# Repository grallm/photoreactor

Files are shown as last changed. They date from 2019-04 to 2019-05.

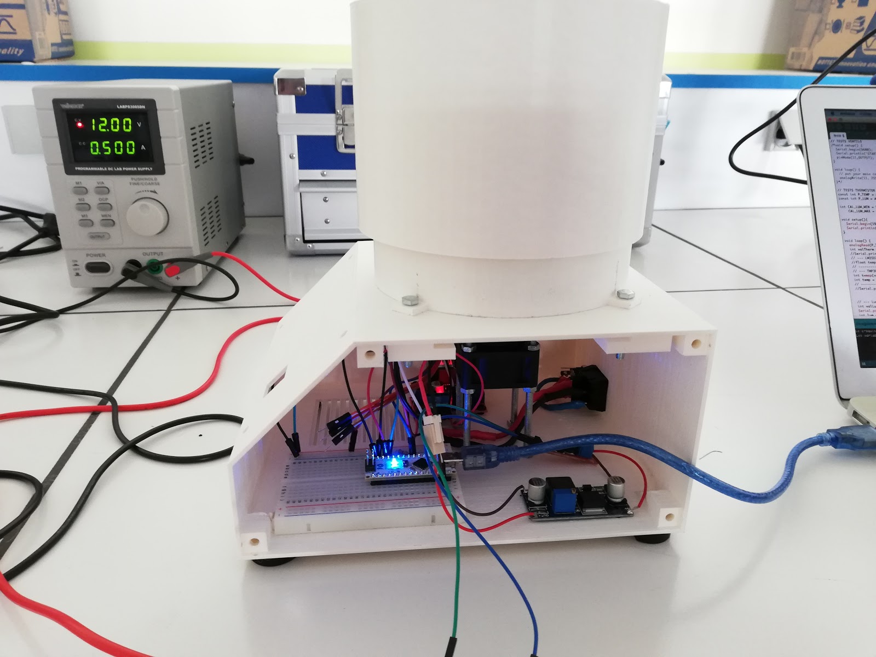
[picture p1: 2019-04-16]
images/finishing_assembly.jpg

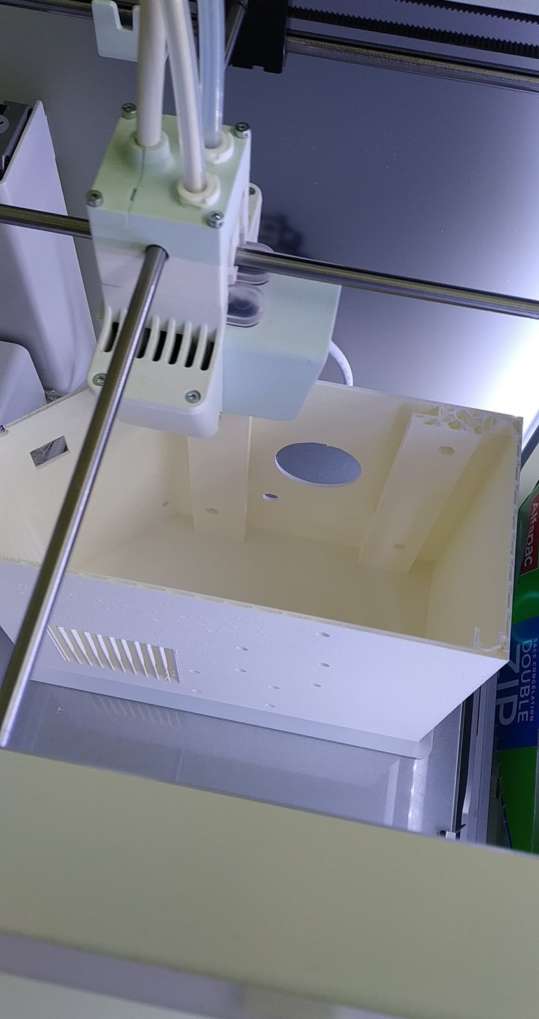
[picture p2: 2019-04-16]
images/box_printing.jpg

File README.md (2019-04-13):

# Photoreactor
Developed in first year of studies to accelerate chemical reactions

Original project https://gitlab.univ-nantes.fr/fablab

## Thanks
- Developed at [Fablab de la Faculté des Sciences de Nantes](https://gitlab.univ-nantes.fr/fablab)
- Requested by [Yann PELLEGRIN (Chemistry researcher at Université de Nantes)](https://www.univ-nantes.fr/version-francaise/yann-pellegrin-357721.kjsp)
- Developed by [Malo GRALL (@grallm)](https://github.com/grallm/), Théo BORDILLON and Moustafa KHEDIM
- With the preciouses advices and help of [Cédric DOUTRIAUX](https://gitlab.univ-nantes.fr/doutriaux-c) and [Frédéric GOUALARD](http://frederic.goualard.net/)

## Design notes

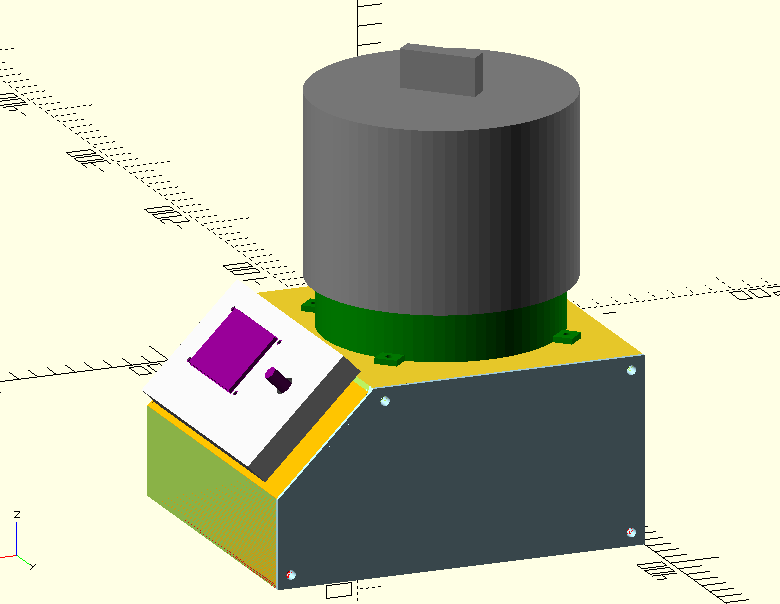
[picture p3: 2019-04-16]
images/fin3D-ext.27-03-19.png

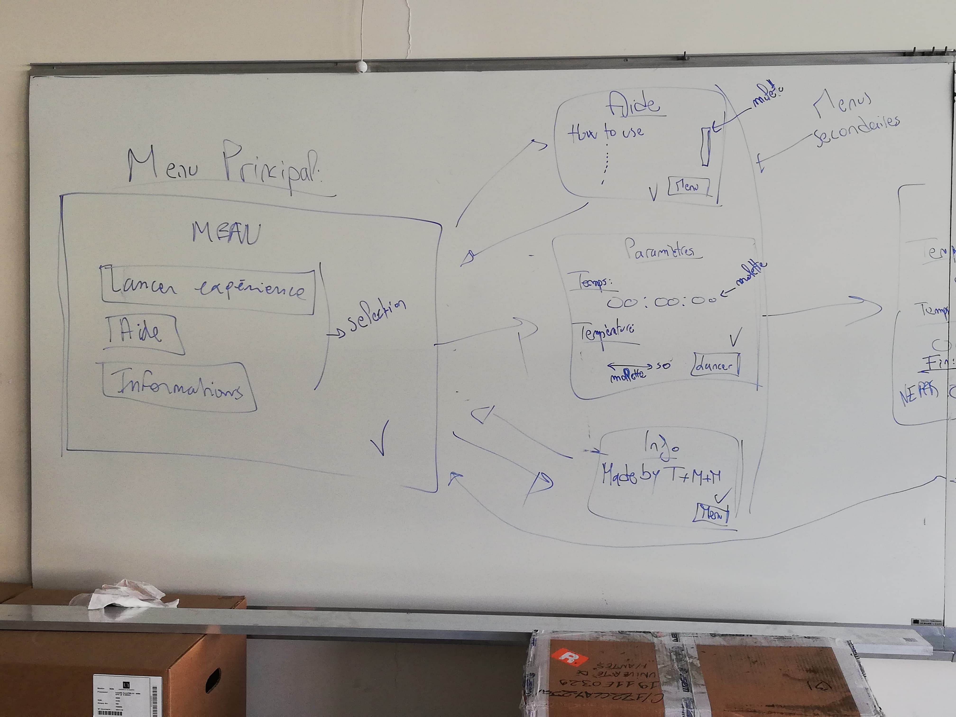
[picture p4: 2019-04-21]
images/menus_schema-1.jpg

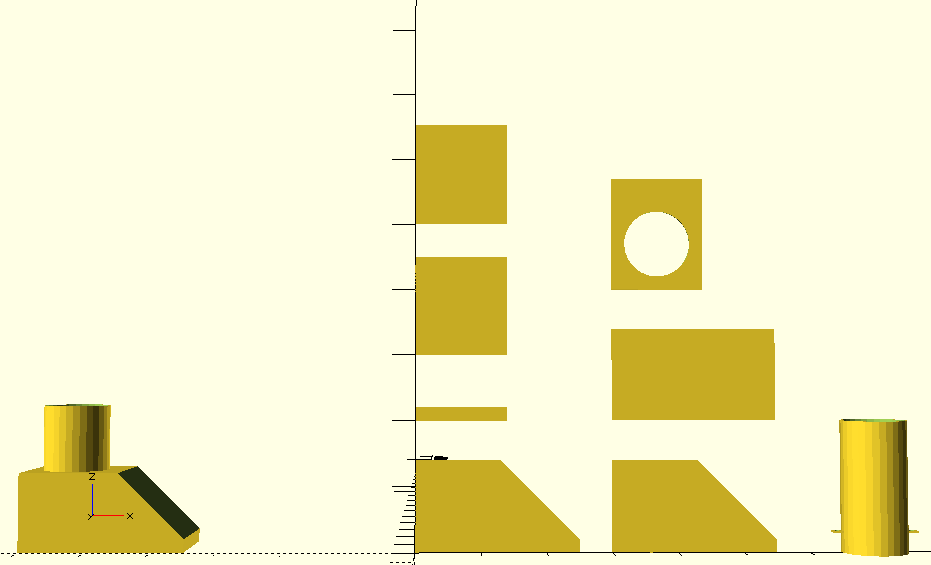
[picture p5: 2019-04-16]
images/Modèle 3D semaine 5.png

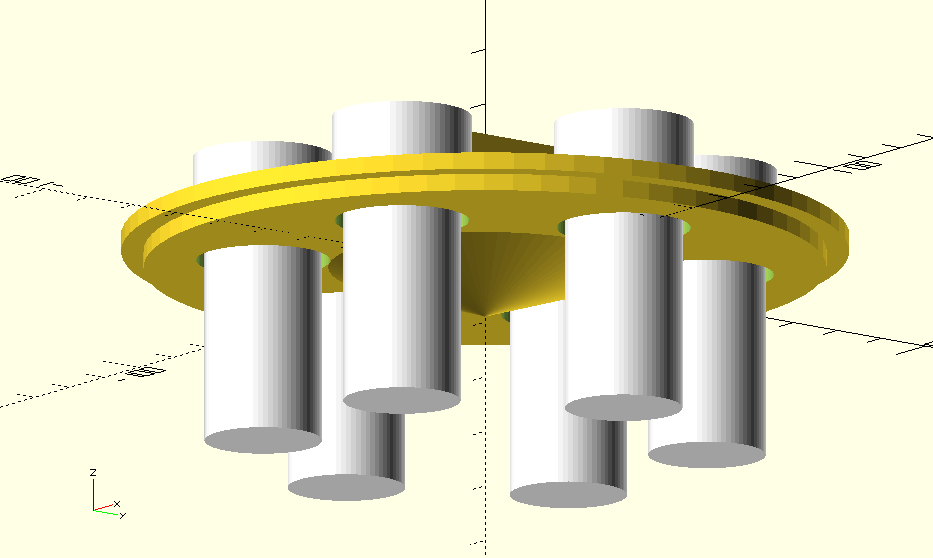
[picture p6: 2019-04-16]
images/grille-S11.png

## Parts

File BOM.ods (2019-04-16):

Projet photoréacteur (Théo Malo et Moustafa) |  |  | Prix total (euros) | 151.08 | Prix total unité (euros) (juste achats) | 91.58
Parties | Produit | Quantité | Lien | Site d'achat | Description | Prix (euros par unité) | Prix total (euros) | Vérifié (stock, coût)
Alimentation | Coupleur pour piles (18650) | 2 | https://www.gotronic.fr/art-coupleur-2-accus-18650-bh538-27840.htm | gotronic.fr | Si pas alimentation direct -> sur piles | 2.4 | 4.8 | OK
 | Piles 18650 | 4 | https://www.gotronic.fr/art-accu-li-ion-18650-2-5a-29250.htm | gotronic.fr | Si pas le droit alimentation | 9.9 | 39.6 | OK
 | OU alimentation 12V |  | https://www.gotronic.fr/art-adaptateur-ps1230-21193.htm | gotronic.fr |  |  | 0 | OK
 | Interrupteur | 1 | https://www.gotronic.fr/art-interrupteur-h8650-4226.htm | gotronic.fr |  | 1.7 | 1.7 | OK
 | Embout femelle pour alimentation (5,5x2,1mm) | 1 | https://www.gotronic.fr/art-embase-alim-sa215-14966.htm | gotronic.fr |  | 0.4 | 0.4 | OK
 | Attache mâle (Molex 2.54mm) | 1 | https://www.gotronic.fr/art-connecteur-s002-90.htm | gotronic.fr | Alimenter tiroir | 0.1 | 0.1 | OK
 | Attache femelle (Molex 2.54mm) | 1 | https://www.gotronic.fr/art-connecteur-p002-91.htm | gotronic.fr | Alimenter tiroir | 0.1 | 0.1 | OK
 | Abaisseur de tension | 3 | https://www.gotronic.fr/art-regulateur-ajustable-1-25-a-30-v-ef03061-23543.htm | gotronic.fr | Baisser tension depuis piles (14->12) et pour LED(12->2.3) | 3.15 | 9.45 | OK
Optique | LED | 2 | https://www.conrad.fr/p/roschwege-led-high-power-bleu-31-lm-130-23-v-700-ma-lsc-b-181827 | conrad.fr |  | 7.4 | 14.8 | OK
 | Radiateur | 1 | https://www.conrad.fr/p/dissipateur-pour-led-fischer-elektronik-sk-46-10-sa-10020378-24-kw-l-x-l-x-h-51-x-51-x-10-mm-1-pcs-188053 | conrad.fr | Accrocher LED dessus (pâte)(sur tiroir) | 1.93 | 1.93 | OK
 | Graisse conductrice | 1 | https://www.gotronic.fr/art-graisse-silicone-t12-5-6044.htm | gotronic.fr | Accrocher LED-radiateur | 2.5 | 2.5 | OK
 | Ventilateur | 1 | https://www.gotronic.fr/art-mf30101v2-28970.htm | gotronic.fr | Sous radiateur | 8.2 | 8.2 | OK
 | Pilote LED | 2 | https://www.gotronic.fr/art-driver-de-led-de-puissance-com-13716-24815.htm | gotronic.fr | Controler LED depuis Arduino | 8.4 | 16.8 | OK
 | Bornier à vis 3,5mm | 1 | https://www.gotronic.fr/art-bornier-sc02-3-5-15470.htm | gotronic.fr | Utiliser LED 350 ou 700mA | 0.4 | 0.4 | OK
Contrôle | Ecran OLED | 1 | https://www.gotronic.fr/art-afficheur-lcd-i2c-grove-114990502-24517.htm#complte_desc | gotronic.fr |  | 21.9 | 21.9 | OK
 | Controleur ventilateur (=moteurs) + alimentation Arduino | 1 | https://www.gotronic.fr/art-commande-de-2-moteurs-sbc-motodriver2-27418.htm | gotronic.fr | Alimenter Arduino + contrôler ventilateur depuis Arduino | 6.9 | 6.9 | OK
 | Thermistor | 3 | https://www.gotronic.fr/art-tmp36-19559.htm | gotronic.fr | Vérifier bon fonctionnement | 1.95 | 5.85 | OK
 | Photoresistance | 3 | https://www.gotronic.fr/art-photoresistance-ldr04-2150.htm | gotronic.fr | Vérifier bon fonctionnement | 0.7 | 2.1 | OK
 | Arduino Nano | 1 | https://www.gotronic.fr/art-carte-nano-3-0-26126.htm | gotronic.fr |  | 8.9 | 8.9 | OK
 | Encodeur rotatif/s'appuie | 1 | https://www.gotronic.fr/art-encodeur-ec12plrvfd24-20743.htm | gotronic.fr | Séléctionner menus/paramètres | 4.65 | 4.65 | OK

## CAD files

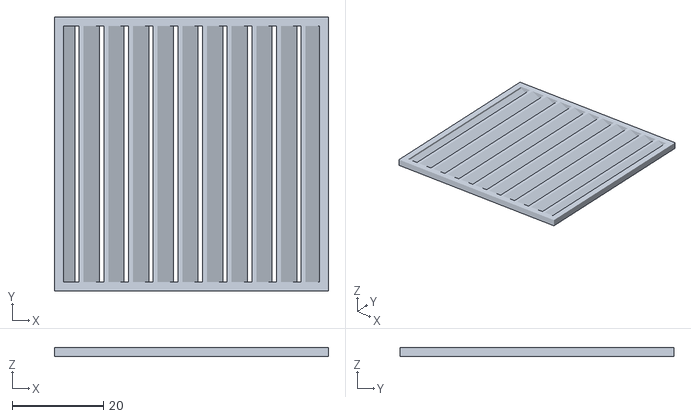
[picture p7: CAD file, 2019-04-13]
3D-openscad/ventilo-grille-lames.stl
60.0 x 60.0 x 2.00

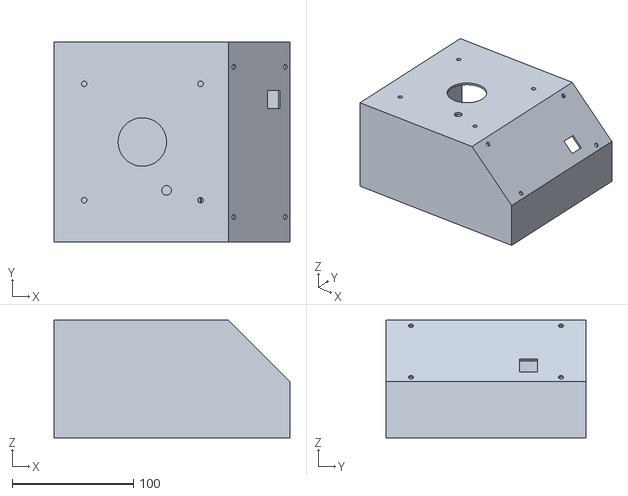
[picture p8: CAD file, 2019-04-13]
toprint_models/boite-ensemble.stl
195.0 x 165.0 x 97.5

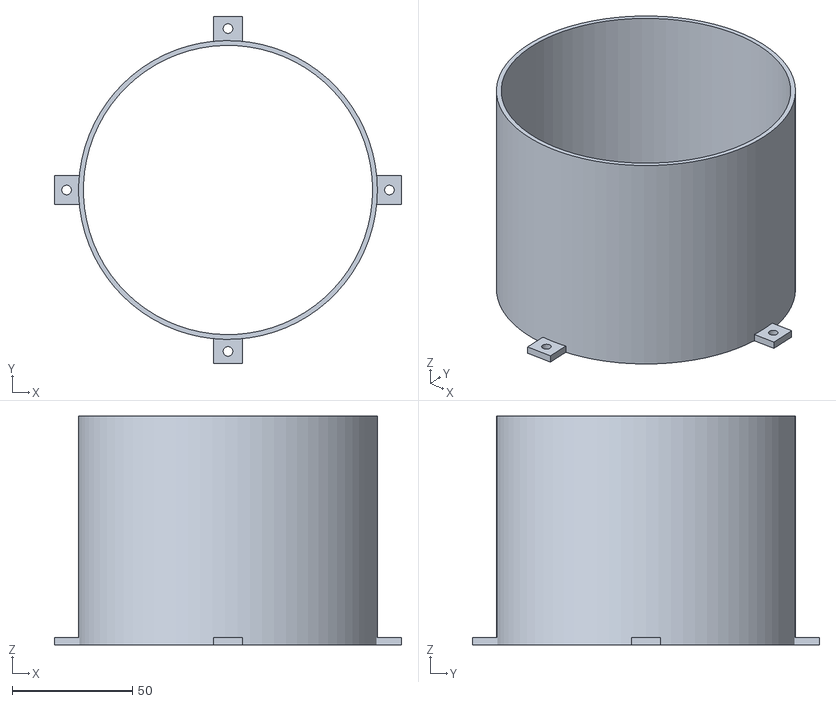
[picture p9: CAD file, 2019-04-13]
toprint_models/cylindre.stl
144.0 x 144.0 x 95.0

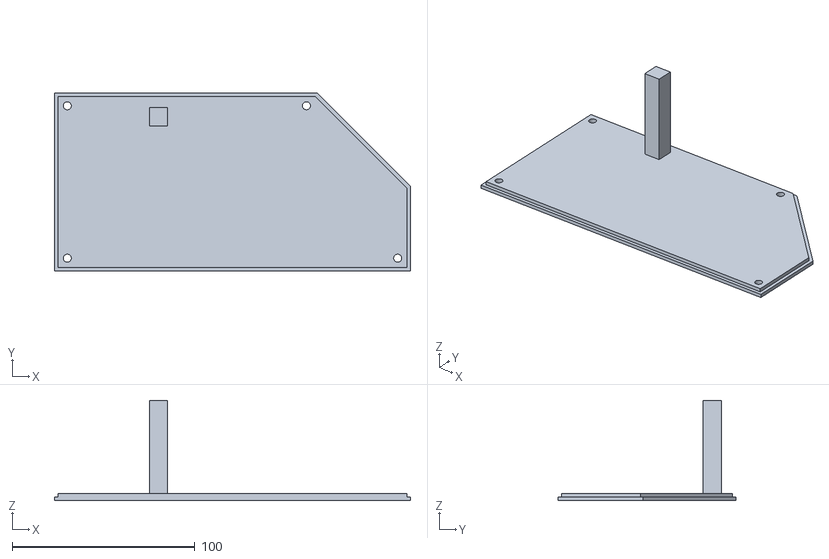
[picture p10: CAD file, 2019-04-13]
toprint_models/droite-ferme.stl
195.0 x 97.5 x 55.0

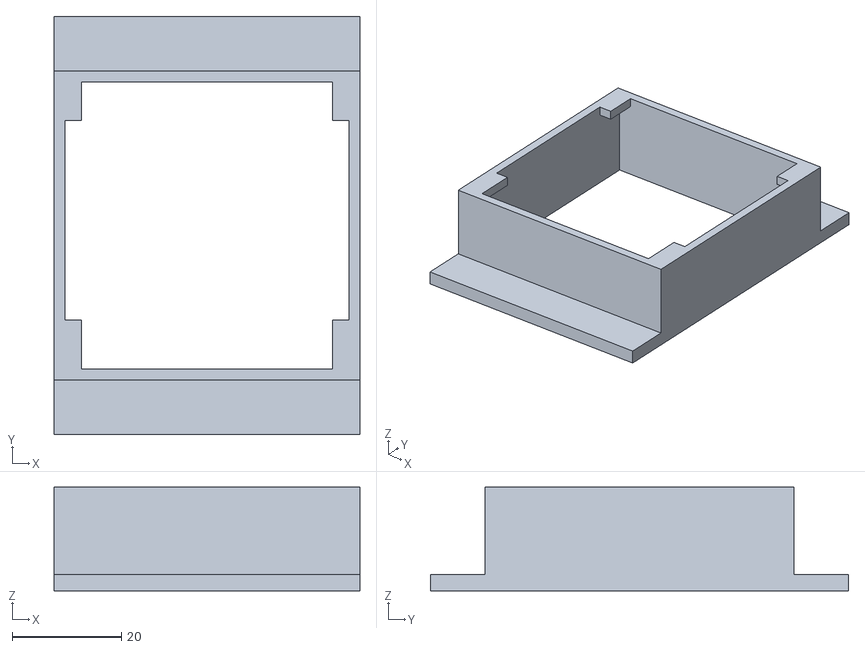
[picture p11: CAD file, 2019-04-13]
toprint_models/tiroir.stl
56.0 x 76.5 x 19.0

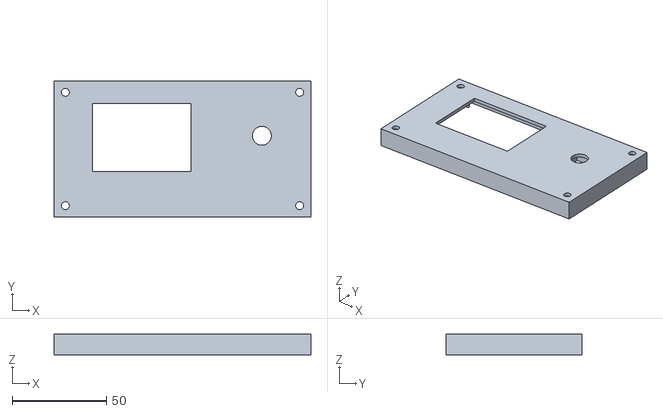
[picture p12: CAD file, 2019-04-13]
toprint_models/capot_ecran.stl
136.0 x 72.0 x 11.0

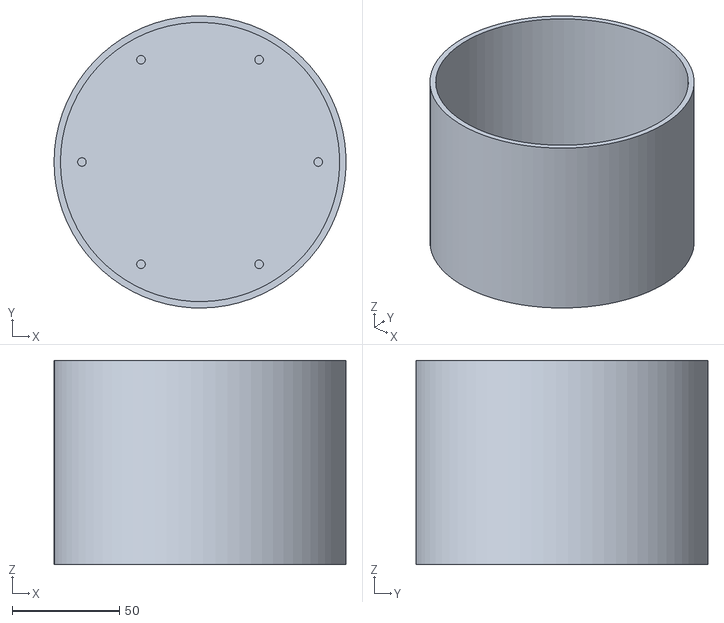
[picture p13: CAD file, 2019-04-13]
toprint_models/capuchon.stl
135.9 x 136.0 x 95.0

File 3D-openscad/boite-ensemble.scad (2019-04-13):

use <tubes-bouchons.scad>;
use <cylindre-grille.scad>;
use <modules_achetes.scad>;
use <tiroir_radiateur.scad>;
use <capot_ecran.scad>;

include <nutsnbolts/cyl_head_bolt.scad>;

$fn=75;

largeur=152 + 2*4 + 5;
longueur=195;
hauteur=95/2 + 50;
longueurHaut=126+20;
rTrouVis=2.2;

/*
-= inverser bBoard et trou ventilateur
-= réduire taille trou ventilo
-= pavés pour visser côtés (trou vis long + trou écrou)
-= afficher tiroir
*/


module fond(){
    /*
    -= place pour tous composants -> gérer espace
    -= trous pour composants
    -= trous ventilo
    - pieds (coller caoutchouc ?)
    -= trous N&B pour fixer face gauche
    */
    union(){
        difference(){
            cube([longueur,largeur,2]);
            translate([longueur-80,20,-1]){
                cube(60,6);
            }
            
            // Trous Abaisseur
            translate([20+48,largeur-23-10,0]){
                rotate(90){
                    translate([1.6+1,6+1,-1]) cylinder(5,rTrouVis,rTrouVis);
                    translate([23-1.6-1,48-6-1,-1]) cylinder(5,rTrouVis,rTrouVis);
                }
            }
            // Trous ventilateur
            translate([longueurHaut/2-40/2,largeur/2-40/2]){
                translate([4,4,-1]) cylinder(5,rTrouVis,rTrouVis);
                translate([40-4,4,-1]) cylinder(5,rTrouVis,rTrouVis);
                translate([4,40-4,-1]) cylinder(5,rTrouVis,rTrouVis);
                translate([40-4,40-4,-1]) cylinder(5,rTrouVis,rTrouVis);
            }
            // Trous contrôleur ventilateur
            translate([70,10,0]){
                translate([43.5-1.9-2,1.9+2,-1]) cylinder(5,rTrouVis,rTrouVis);
                translate([1.9+2,43.5-1.9-2,-1]) cylinder(5,rTrouVis,rTrouVis);
                translate([1.9+2,1.9+2,-1]) cylinder(5,rTrouVis,rTrouVis);
                translate([43.5-1.9-2,43.5-1.9-2,-1]) cylinder(5,rTrouVis,rTrouVis);
            }
        }
        
        // Grille avec "lames" à l'avant
        translate([longueur-20,20+60,0]){
            rotate([0,0,180]){
                import("ventilo-grille-lames.stl");
            }
        }
        
        // Supports pour fixer face gauche
         // Bas Droite
        translate([2+10,largeur-32,10+2]){
            rotate([0,180,0]){
                difference(){
                    cube([10,30,10]);
                    translate([-1,0,-25]) rotate([55,0,0]) cube([30,30,30]);
                    
                    translate([5,34,5]){
                        // Trou vis
                        rotate([90,0,0]) cylinder(20,rTrouVis,rTrouVis);
                        // Trou écrou
                        //translate([0,-11.5,0]) rotate([90,90,0]) nutcatch_sidecut("M4", l=20, clk=-.1);
                        translate([0,-30,0]) rotate([90,90,0]) nutcatch_parallel("M4", l=23, clk=-.1);
                    }
                }
            }
        }
         // Bas Gauche
        translate([longueur-2,largeur-32,10+2]){
            rotate([0,180,0]){
                difference(){
                    cube([10,30,10]);
                    translate([-1,0,-25]) rotate([55,0,0]) cube([30,30,30]);
                    
                    translate([5,34,5]){
                        // Trou vis
                        rotate([90,0,0]) cylinder(20,rTrouVis,rTrouVis);
                        // Trou écrou
                        //translate([0,-11.5,0]) rotate([90,90,0]) nutcatch_sidecut("M4", l=20, clk=-.1);
                        translate([0,-30,0]) rotate([90,90,0]) nutcatch_parallel("M4", l=23, clk=-.1);
                    }
                }
            }
        }
    }
}

module arriere(){
    /*
    */
    
    difference(){
        cube([hauteur-4,largeur,2]);
        // Interrupteur
        translate([5,40,-1]){
            cube([20,23,10]);
        }
        // Alim femelle
        translate([12.5,25,-1]){
            cylinder(10,9/2,9/2);
        }
    }
}

module faceEcran(){
    /*
    -= trou cables écran + encodeur
    -= trous attachent écran
    */
    
    largHauteur=longueur-longueurHaut; // (h=l=49)
    longueurCalc=sqrt(2*pow(largHauteur,2))+5; // 69.3
    
    difference(){
        cube([longueurCalc-2,largeur,2]);
        
        // Trous vis
        translate([72,largeur/2-136/2,-1]){
            rotate(90){
                translate([6,6,0]){
                    cylinder(5,2.1,2.1);
                }
                translate([136-6,6,0]){
                    cylinder(5,2.1,2.1);
                }
                translate([6,72-6,0]){
                    cylinder(5,2.1,2.1);
                }
                translate([136-6,72-6,0]){
                    cylinder(5,2.1,2.1);
                }
            }
        }
        // Trou câbles
        translate([45,110,-1]){
            cube([15,15,4]);
        }
    }
}

module face(){
    cube([hauteur-4-(longueur-longueurHaut),largeur,2]);
}

module haut(){
    /*
    -= rails pour tiroir
    -= trous N&B vis et écrou pattes cylindre
    -= vérifier trous écrous N&B
    -= trous face gauche
    -= trou pour faire passer câbles thermomètre et photorésistance
    */
    R=63+7; // R cylindre
    rTrou=2.3; // R trous vis
    //lLang=;
    
    difference(){
        union(){
            cube([longueurHaut,largeur,2]);
            
            // Rails tiroir + trous écrous cylindre
            translate([0,0,-10]){
                // Droite (X ligne trous = longueurHaut/2-60+12)
                translate([longueurHaut/2-60+12-10,0,0]){
                    difference(){
                        cube([27,largeur-7,10]);
                        // Rail
                        translate([17,52,5]){
                            cube([50,largeur+10,5]);
                        }
                    }
                }
                // Gauche (X ligne trous = longueurHaut/2+60-12)
                translate([longueurHaut/2+60-12-17, ,0]){
                    difference(){
                        cube([27,largeur-7,10]);
                        // Rail
                        translate([-1,52,5]){
                            cube([10,largeur+10,5]);
                        }
                    }
                }
            }
            // Blocs pour fixer face détachée
            // Haut Droite
            translate([2,largeur-32,-10]){
                difference(){
                    cube([10,30,10]);
                    translate([-1,0,-25]) rotate([55,0,0]) cube([30,30,30]);
                    
                    translate([5,0,5]){
                        // Trou vis
                        translate([0,35,0]) rotate([90,0,0]) cylinder(20,rTrouVis,rTrouVis);
                        
                        // Trou écrou
                        rotate([90,0,0]) nutcatch_parallel("M4", l=25, clk=-.1);
                        //translate([0,-11.5,0]) rotate([90,90,0]) nutcatch_sidecut("M4", l=20, clk=-.1);
                    }
                }
            }
            // Haut Gauche
            translate([longueurHaut-3-10,largeur-32,-10]){
                difference(){
                    cube([10,30,10]);
                    translate([-1,0,-25]) rotate([55,0,0]) cube([30,30,30]);
                    
                    translate([5,0,5]){
                        // Trou vis
                        translate([0,35,0]) rotate([90,0,0]) cylinder(20,rTrouVis,rTrouVis);
                        // Trou écrou
                        rotate([90,0,0]) nutcatch_parallel("M4", l=25, clk=-.1);
                        //translate([0,-11.5,0]) rotate([90,90,0]) nutcatch_sidecut("M4", l=20, clk=-.1);
                    }
                }
            }
        }
        
        translate([longueurHaut/2,largeur/2,0]){
            // Trou LED cylindre
            translate([0,0,-1]) cylinder(6,20,20);
        
            // Trou thermomètre + photorésistance
            translate([20,-40,-1]) cylinder(4,4,4);
            
            // Trous attaches cylindre
            // 4 pattes
            rotate(45){
                for(i=[1:1:4]){
                    translate([(R-2)*cos(i*90),(R-2)*sin(i*90),-15]){
                        cylinder(20,rTrou,rTrou);
                        translate([0,0,+13]) nutcatch_parallel("M4", l=50, clk=-.1);
                        // Trou écrou
                        rotEc = (i==3 || i==4) ? 135 : -45;
                        //translate([0,0,14]) rotate(rotEc) nutcatch_sidecut("M4", l=20, clk=-.1);
                    }
                }
            }
            // 6 pattes
            /*rotate(60){
                for(i=[1:1:6]){
                    translate([(R-2)*cos(i*60),(R-2)*sin(i*60),0]){
                        cylinder(6,rTrou,rTrou);
                    }
                }
            }*/
        }
    }
}
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

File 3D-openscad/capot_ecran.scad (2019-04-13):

use <modules_achetes.scad>;

$fn=75;

// Capot pour tenir écran + encodeur
module capot(){
    /*
    -= trou écran
    -= trou encodeur
    -= trous attachent écran-capot-boîte
    -= cube creux pour bloquer rotation encodeur
    -= déplacer écran en haut: laisser place gauche et bas pour cable
    */
    union(){
        difference(){
            cube([136,72,11]);
            translate([2,2,-1]){
                cube([132,68,10]);
            }
            // Trou encodeur
            translate([130-20,43,7]){
                cylinder(5,5,5);
            }
            // Trou écran
            translate([20.5,72-37.83-10,7]){
                cube([52,36,5]);
            }
            // Trous vis pour accrocher capot
            translate([6,6,8]){
                cylinder(5,2.1,2.1);
            }
            translate([136-6,6,8]){
                cylinder(5,2.1,2.1);
            }
            translate([6,72-6,8]){
                cylinder(5,2.1,2.1);
            }
            translate([136-6,72-6,8]){
                cylinder(5,2.1,2.1);
            }
        }
        // Pins pour accrocher écran
        translate([15-.1,72-39-10,9]){
            translate([0.9+1.2,1.2+1.2,-4]){
                cylinder(4,1,1);
            }
            translate([63.27-0.9-1.2,1.2+1.2,-4]){
                cylinder(4,1,1);
            }
            translate([63.27-0.9-1.2,38-1.2-1.2,-4]){
                color("red") cylinder(4,1,1);
            }
            translate([0.9+1.2,38-1.2-1.2,-4]){
                color("red") cylinder(4,1,1);
            }
        }
        // Cube bloque encodeur
        difference(){
            translate([130-20-8.25,43-8,4]){
                cube([16.5,16,7]);
            }
            translate([130-20-7.25,43-7,2]){
                cube([14.5,14,10]);
            }
        }
    }
}


capot();
//translate([130-20-7,43-6.75,4]) encodeur();
//ecran ();
//translate([15-.1,72-37.83-10-.7,2.5]) ecran();

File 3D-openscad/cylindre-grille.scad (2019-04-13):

use <tubes-bouchons.scad>;
$fn = 75;

/*
    -= détacher poignée -> coller
    -= trous d'aération entre tubes collés extérieur
    -= capuchon descendant avec 2mm de jour
    -= 4 pattes d'accroche (6 bloquent tiroir + trop long)
    - capote pour écran et encodeur
*/


// Grille tenir tubes: 120x15
module supportTubes() {
    R = 60; // rayon support (+1cm)
    rTrous = 12; // rayons des trous pour tubes (+1mm)
    rPosTrous=40; // Rayon sur lequel trous positionnés
    hCone=9;
    rCone=28;
    
    union(){
        difference(){ // Trous + surface
            union(){
                translate([0,0,3]){
                    cylinder(3, R+3, R+3);
                }
                cylinder(3, R-1, R-1);
            }
            for(i=[0:1:7]){
                translate([rPosTrous*cos(i*60),rPosTrous*sin(i*60),-0.5]){
                    cylinder(10, rTrous,rTrous);
                }
            }
            
            // Trous aération
            for(i=[-1:2:1]){
                translate([50*cos(i*30),50*sin(i*30),-0.5]){
                    cylinder(10,3,3);
                }
                translate([50*cos(i*150),50*sin(i*150),-0.5]){
                    cylinder(10,3,3);
                }
                translate([50*cos(i*90),50*sin(i*90),-0.5]){
                    cylinder(10,3,3);
                }
            }
        }
        translate([0,0,-hCone]){ // Cône de réflexion
            cylinder(hCone,0,rCone);
        }
    }
}

module poignee(){
    // Languette pour grille + capuchon
    cube([10,40,20]);
}

// Cylindre pour pilluliers: 152(126+2*13)x95 (languettes: h=H/2 l=15)
module cylindrePilluliers(){
    R=62; // R grille + épaisseur
    H=95;
    lLanguette=12;
    hLang=0;
    rTrou=2;
    
    difference(){
        union(){
            cylinder(H,R,R);
            
            // 4 pattes
            for(i=[1:1:4]){
                translate([(R-2)*cos(i*90),(R-2)*sin(i*90),0]){
                    rotate(i*90){
                        translate([0,-lLanguette/2,0]){
                            difference(){
                                
                                cube([lLanguette,lLanguette,3]);
                                translate([lLanguette/2+1,lLanguette/2,-1]){
                                    cylinder(5,rTrou,rTrou);
                                }
                            }
                        }
                    }
                }
            }
            
            // 6 pattes
            /*for(i=[1:1:6]){
                translate([(R-2)*cos(i*60),(R-2)*sin(i*60),0]){
                    rotate(i*60){
                        translate([0,-lLanguette/2,0]){
                            difference(){
                                
                                cube([lLanguette,lLanguette,3]);
                                translate([lLanguette/2+1,lLanguette/2,-1]){
                                    cylinder(5,rTrou,rTrou);
                                }
                            }
                        }
                    }
                }
            }*/
        }
        /*translate([0,0,-5]){
            cylinder(H+10,R-3,R-3);
        }*/
        
        // Creux
        translate([0,0,-1]){
            cylinder(H+5,R-2,R-2);
        }
        // Fond
        /*translate([0,0,-3]){
            cylinder(H+6,R/2,R/2);
        }*/
    }
}

module capuchon(){
    H=95;
    R=61+5;
    rPosPieds=55;
    hPieds=20;
    rPieds=2;
    
    union(){
        difference(){
            cylinder(H,R,R);
            
            // Creux
            translate([0,0,-1]){
                cylinder(H-2,R-2,R-2);
            }
        }
        
        // Pieds
        for(i=[1:1:6]){
            translate([rPosPieds*cos(i*60),rPosPieds*sin(i*60),H-hPieds-3]){
                cylinder(hPieds,rPieds,rPieds);
            }
        }
    }
}


module ensembleCylindre(){
    translate([0,0,92]){
        supportTubes();
        translate([-5,-20,6]){ // Languette grille
            poignee();
        }
        
        // Dessiner cercle de 8 tubes
        for(i=[0:1:7]){
            translate([40*cos(i*60),40*sin(i*60),-8]){
                color("white") tubeGrosBouchon();
            }
        }
        
        translate([-5,-20,29]){ // Languette capuchon
            color("gray") poignee();
        }
    }

    color("green") cylindrePilluliers();
    
    translate([0,0,26]){
        color("gray") capuchon();
    }
}


//rotate([180,0,0]){
//supportTubes();
//}
//translate([70,0,-1]){
//    rotate([0,90,0]){
//poignee();
//}}
//cylindrePilluliers();

rotate([0,180,0]){
    capuchon();
}

//ensembleCylindre();

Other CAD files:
3D-openscad/modules_achetes.scad
3D-openscad/nutsnbolts/cyl_head_bolt-drawAllScript.scad
3D-openscad/nutsnbolts/cyl_head_bolt.scad
3D-openscad/nutsnbolts/data-access.scad
3D-openscad/nutsnbolts/data-metric_cyl_head_bolts.scad
3D-openscad/nutsnbolts/examples.scad
3D-openscad/nutsnbolts/materials.scad
3D-openscad/tiroir_radiateur.scad
3D-openscad/tubes-bouchons.scad
3D-openscad/ventilation.scad

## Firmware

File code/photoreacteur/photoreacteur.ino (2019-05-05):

// Code photoréacteur 1.0
const String version = "1.0";
const String version_hardware = "1.0";
/*
 * PRIORITY
 * - Faire fonctionner la lecture du thermomètre
 * - calibrer thermomètre
 * - Utiliser floats pour température
 * - Différence lumière non fonctionnelle
 * 
 * TODO
 * - Remettre en place blocage depuis thermomètre et photorésistance
 * - Gestion température
 * - Gestion température et Luminosité moyennes
 * - Vérifier si le thermomètre est fonctionnel
 * - Trouver d'où vient le saut entre secondes et minutes (quand baisse secondes)
 * - Afficher température en pause et lors rotation -> variables globales
 * - Vérifier arrondi température
 * 
 *
 * AMÉLIORATIONS
 * - Passer de 60s à 1mn et 60mn à 1h
 * - Bonne gestion ventilateur selon température
 * - Meilleure actualisation écran -> refresh que les parties nécessaires
 * - Message "NE PAS OUVRIR !!!" lorsqu'en réaction
 * - Veille écran
 * - optimiser le nombre/type de variables et d'expressions
 * - Plus grande différence de température
 * - Faire fonctionner les erreurs de température et de lumière
 * - Faire plus grande différence de température et de lumière
 * - N'actualiser que les données sur le M_Started -> pas les boutons pause et arrêter
 * - Calibrer le thermomètre
 * - Corriger clignotement
 * - Meilleur curseur (menu principal, started, duration)
 */

#include <Wire.h>
#include <I2C_LCD.h>

I2C_LCD LCD;
uint8_t I2C_LCD_ADDRESS = 0x51; // Adresse écran

/* CONFIGURATION */
const short luminosite = 100, // en %
    LED_R = 6, // Pin LED encodeur rouge
    LED_G = 5, // Pin LED encodeur verte
    LED_HP = 9, // Pin contrôle LED haute puissance
    VENTILO = 11, // Pin contrôle ventilo
    ENC_ROT_1 = 2, // Encodeur rotatif
    ENC_ROT_2 = 3, // Encodeur rotatif
    ENC_INTERRUPTOR = 4, // Interrupteur
    PIN_THERM = A0, // Pin capteur température
    PIN_LUM = A3, // Pin capteur lumière
    CAL_LUM_MIN = 7,
    CAL_LUM_MAX = 146, // Calibrage Min et Max de la photoresistance slon LED
    DOUBLE_LED_SECU = true; // Double sécurité LED (allumée que lorsqu'en réaction)

// Localisation
String LOC = "home";

// Sélection
bool select = true; // Curseur activé
short CURSOR = 0; // Valeur sélecteur (0 = neutre)
short maxSelect = 3; // Valeur max de sélection (nombre de sélections possibles)

bool select_click = false; // Curseur click activé
short CURSOR_CLICK = 1; // Sélection avec le click
short maxSelect_click = 8; // Valeur max de sélection (nombre de sélections possibles)

// Variables interrupteur
bool pushedPrev = true;
bool pushed = false; // Appuie 1 fois

// Variables de fonctionnement
short duration_val[7] = {0,0,0,0,0,0}; // Temps de durée réglé
unsigned long time_left = 0; // Temps restant en secondes d'expérience
short REACTING = 0; // Etat (0: OFF / 1: ON / 2: To start / >=3: To stop)
short VENTILO_STATE = false; // Etat (0: OFF / 1: ON / 2: To start / >=3: To stop)
short LED_STATE = false; // Etat (0: OFF / 1: ON / 2: To start / >=3: To stop)
unsigned long last_sec_millis = millis(); // Sauvegarde dernière valeur lors décompte 1 seconde
short led_twinkle = 0; // Stocker PIN
bool TWINKLE_STATE = false; // Savoir si éteinte ou allumée
unsigned long last_twinkle = 0; // Stockage millis clignotement pour ne pas clignoter extêmement vite

// Variables capteurs
short start_temp = 0; // Température au démarrage
float moy_temp_accu = 0; // Accumulateur température chaque seconde pour calculer moyenne
float max_diff_temp = 0; // Ecart maximum avec la moyenne
unsigned long moy_lumi_accu = 0; // Accumulateur lumière chaque seconde pour calculer moyenne
short max_diff_lumi = 0; // Ecart maximum avec la moyenne
float temp_mes = -1; // Température mesurée en degrés
int lum_mes = -1; // Valeur mesurée en % capteur lumière



// -- Fonction générales --
// Transformer temps secondes en HH:MM:SS
String time_sec_toStr(unsigned long timeSec){
  unsigned long time[4];
  String timeStr[4];

  // Heures
  time[0] = timeSec/3600;
  timeSec -= 3600*time[0];
  timeStr[0] = String(time[0]);
  timeStr[0] = (time[0]<10)? "0"+timeStr[0] : timeStr[0]; // Rajouter 0 si <10

  // Minutes
  time[1] = timeSec/60;
  timeSec -= 60*time[1];
  timeStr[1] = String(time[1]);
  timeStr[1] = (time[1]<10)? "0"+timeStr[1] : timeStr[1];

  // Secondes
  time[2] = timeSec;
  timeStr[2] = String(time[2]);
  timeStr[2] = (time[2]<10)? "0"+timeStr[2] : timeStr[2];

  // Retourner 00:00:00
  return timeStr[0] +":"+ timeStr[1] +":"+ timeStr[2];
}

// Mettre le temps paramétré en secondes
unsigned long time_to_sec(int* time){
  unsigned long timeSec = 0;

  // Secondes
  timeSec += time[0];
  timeSec += 10*time[1];

  // Minutes
  timeSec += 60*time[2];
  timeSec += 10*60*time[3];

  // Heures
  timeSec += 3600*time[4];
  unsigned long temp_time = time[5]; // Dépassement de capacité
  timeSec += 10*(3600*temp_time);

  return timeSec;
}
// ----------------



// -- Fonctions de formattage --
// Donne X pour placer texte centre, droite ou gauche (Gauche=L, Droite=R, Centre=C) (donner le texte et la hauteur des lettres)
int FF_placeX(String text, int fontX, String place = "C"){
  if(place=="C"){
    return 128/2-text.length()*fontX/2-1;
  }else if(place=="R"){
    return 128-text.length()*fontX-1;
  }else{
    return 0;
  }
}

// Donne Y pour centrer texte (Haut=T, Bas=B, Centre=C)
int FF_placeY(String text, int fontY, String place = "T"){
  if(place=="C"){
    return 64/2-fontY/2-1;
  }else if(place=="B"){
    return 63-fontY-1;
  }else{
    return 0;
  }
}
// ----------------


// -- Fonctions de menus --
int MF_spacing_title = 6; // Nombre de pixels entre titre et texte
int MF_spacing = 2; // Nombre de pixels entre chaque ligne
int MF_spacing_button = 2; // Nombre de pixels après bouton
int MF_pos[3] = {0,0}; // Position d'écriture dans les menus

bool refreshScreen = false; // Rafraichissement de l'écran

// Réinitialiser la position et nettoyer écran
void MF_reset(){
  LCD.CleanAll(WHITE);
  LCD.CursorConf(OFF, 0);
  MF_pos[0]=0;
  MF_pos[1]=0;
  refreshScreen = false;
}

// Configurer les variables des LEDs selon Menu
void MF_leds(int led, bool twinkle = false){
  digitalWrite(LED_G, LOW);
  digitalWrite(LED_R, LOW);

  digitalWrite(led, HIGH);
  if(twinkle){
    led_twinkle = led;
    TWINKLE_STATE = true;
  }else{
    led_twinkle = 0;
  }
}

// Titre d'un menu
void MF_title(String text){
  LCD.FontModeConf(Font_6x8, FM_ANL_AAA, BLACK_NO_BAC);
  
  LCD.DispStringAt(text.c_str(), FF_placeX(text,6), 0);
  
  MF_pos[0]=0;
  MF_pos[1]=8+MF_spacing_title;
}

// Ecrire du texte avec balises et params (placer texte X et Y)
void MF_text(String text, String place = "HL", bool jump=true){
  LCD.FontModeConf(Font_6x8, FM_ANL_AAA, BLACK_NO_BAC);

  int posX = 0;
  int posY = MF_pos[1];
  if(place=="BR"){ // Placer le texte
    posX = FF_placeX(text,6,"R");
    posY = FF_placeY(text,8,"B");
  }else if(place=="C"){
    posX = FF_placeX(text,6,"C");
  }else if(place=="BL" || place=="B"){
    posY = FF_placeY(text,8,"B");
  }else if(place == "R"){
    posX = FF_placeX(text,6,"R");
  }
  
  LCD.DispStringAt(text.c_str(), posX, posY);
  
  MF_pos[0]=0;
  if(jump){
    MF_pos[1]+=8+MF_spacing;
  }
}
// Ecrire du texte plus gros
void MF_text_big(String text, String place = "HL"){
  LCD.FontModeConf(Font_8x16_1, FM_ANL_AAA, BLACK_NO_BAC);

  int posX = 0;
  int posY = MF_pos[1]-2;
  if(place=="BR"){ // Placer le texte
    posX = FF_placeX(text,8,"R");
    posY = FF_placeY(text,16,"B");
  }else if(place=="C"){
    posX = FF_placeX(text,8,"C");
  }else if(place=="BL" || place=="B"){
    posY = FF_placeY(text,16,"B");
  }
  
  LCD.DispStringAt(text.c_str(), posX, posY);
  
  MF_pos[0]=0;
  MF_pos[1]+=14;
}

// Boutton avec cadre, noir si sélectionné
void MF_button(String text, bool select = false, String place="C", bool jump=true){
  int posX=2;
  int posY=MF_pos[1];
  if(place=="C"){ // Centrer le texte
    posX = FF_placeX(text,6);
  }else if(place=="BR"){
    posX = FF_placeX(text,6, "R")-2;
    posY = FF_placeY(text,8, "B")-2;
  }else if(place=="BL"){
    posY = FF_placeY(text,8, "B")-2;
  }
  
  if(select){ // Si sélectionné carré rempli
    LCD.DrawRectangleAt(posX-2, posY, 4+text.length()*6, 4+8, BLACK_FILL);
  }else{
    LCD.DrawRectangleAt(posX-2, posY, 4+text.length()*6, 4+8, BLACK_NO_FILL);
  }
  
  if(select){ // Si sélectionné écrit en blanc
    LCD.FontModeConf(Font_6x8, FM_ANL_AAA, WHITE_NO_BAC);
  }else{
    LCD.FontModeConf(Font_6x8, FM_ANL_AAA, BLACK_NO_BAC);
  }

  LCD.DispStringAt(text.c_str(), posX, posY+2);

  if(jump){
    MF_pos[1]+=12+MF_spacing_button;
  }
}
// ----------------


// -- Les menus --
// Menu principal avec quel bouton sélectionné (0=aucun, 1-3)
void M_Menu(int selected = 0){
  LOC = "home";
  select = true;
  maxSelect = 2;
  MF_leds(LED_G);
  MF_reset();
  MF_title("MENU");
  MF_button("Lancer Experience", (selected==1)? true:false);
  MF_button("Infos", (selected==2)? true:false);
  MF_text("v"+version, "BR");
}

// Fin d'expérience
/* TODO
 * - Afficher temp et lum moy
 */
void M_Finish(unsigned long time, bool aborted = false, String moy_temp = "??", String moy_perc_lum = "??"){
  LOC = "finish";
  select = false;
  MF_leds(LED_G);
  MF_reset();
  MF_title("EXPERIENCE TERMINEE");
  MF_text("Temps d'exposition", "C");
  MF_text(time_sec_toStr(time), "C");
  MF_text("Temp. moy.: "+ moy_temp +" C"); // 
  MF_text("Lumi. moy.: "+ moy_perc_lum +" %");
  if(aborted){
    MF_text("ARRETEE", "C");
  }
}

// En cours de réaction
void M_Started(int selected=0, bool pause = false, String temp = "??", String perc_lum = "??"){
  LOC = "started";
  select = true;
  maxSelect = 2;
  MF_leds(LED_G, (pause)?false:true);
  MF_reset();
  String pause_txt = (pause)? "PAUSE" : "REACTION EN COURS...";
  MF_title(pause_txt);
  MF_text("Passe: "+ time_sec_toStr(time_to_sec(duration_val)-time_left) +"  |  "+ String(map(time_to_sec(duration_val)-time_left, 0,time_to_sec(duration_val), 0,100)) +"%");
  MF_text("Restant: "+ time_sec_toStr(time_left));
  MF_text("Fin: "+ time_sec_toStr(time_to_sec(duration_val)));
  MF_text("Temp: "+ temp +"C", "L", false);
  MF_text("Lum: "+ perc_lum +"%", "R");
  pause_txt = (pause)? "Reprendre" : "Pause";
  MF_button(pause_txt, (selected==1)? true:false, "BL", false);
  MF_button("Arreter", (selected==2)? true:false, "BR");
}
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

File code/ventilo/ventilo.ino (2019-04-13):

// Contrôle ventilateur
// Paramètres
int ecart_temp = 1; // Ecart de température durant l'expérience avec la température de départ

// Constantes
const
int CAL_LUM_MIN = 0,
    CAL_LUM_MAX = 1023, // Calibrage Min et Max de la photoresistance
    CAL_LUM_ON = 1023, // Calibrage lorsque LED allumée (en %)
    CAL_VENTILO_MIN = 0,
    CAL_VENTILO_MAX = 180, // Calibrage Min et Max de la photoresistance
    VENTILO_PUISS_DEF = 10, // Vitesse ventilo lorsque température bonne pour garder température fixe
    // Pins
    P_VENTILO = 11,
    P_TEMP = A4, // Pin du capteur de température
    P_LUM = A5; // Capteur de lumière

// Variables utiles
float init_temp;

// -- Fonctions Ventilo --
// Allumer le ventilateur à une certaine puissance
void Ventilo(int puissance = 0){
  int puissInt = map(puissance, 0,100, CAL_VENTILO_MIN,CAL_VENTILO_MAX); // Puissance en pourcentage vers intensite
  analogWrite(P_VENTILO, puissInt);
}
// -------

void setup() {
  Serial.begin(9600);
  Serial.println("START");

  pinMode(P_VENTILO, OUTPUT);

  // Température initiale au démarrage
  analogRead(P_TEMP); // Lecture dans le vide car valeur inexacte
  int valTherm = analogRead(P_TEMP);
  // --- LM35DZ
  init_temp = valTherm * (5.0 / 1023.0 * 100.0);
  // ----------
  // --- TMP36
  //int t=map(valTherm,0,1023,0,5000);// Tension entre 0 et 5000 mV
  //init_temp = map(t,0,1750,-50,125); // Tension de 0 à 1750mV en température de -50°C à 125°C;
  // ----------
  Serial.println(init_temp);
}

void loop() {
  // --- Température - thermistor ---
  analogRead(P_TEMP); // Lecture dans le vide car valeur inexacte
  int valTherm = analogRead(P_TEMP);
  // --- LM35DZ
  float temp = valTherm * (5.0 / 1023.0 * 100.0); // Conversion en degrés Celsius
  // ----------
  // --- TMP36
  //int t=map(valTherm,0,1023,0,5000);// Tension entre 0 et 5000 mV
  //int temp = map(t,0,1750,-50,125); // Tension de 0 à 1750mV en température de -50°C à 125°C;
  // ----------
  Serial.println(temp);

  // Effets selon température:
  //  > temp init + écart -> 100% ventilateur
  //  > temp init -> 50% ventilateur
  //  < temp init -> 0% ventilateur
  //  bonne temp (+-0.5) -> quel % ? 10% ?
  if(temp > init_temp + ecart_temp){
    /*
     * TODO
     * - éteindre LED
     */
    Ventilo(100);
    
  }else if(temp > init_temp+.5 || temp < init_temp-.5){
    Ventilo(VENTILO_PUISS_DEF);
    
  }else if(temp > init_temp){
    Ventilo(50);
    
  }else if(temp < init_temp){
    Ventilo(0);
    
  }
  // ----------
  

  // --- Luminosité - photorésistance ---
  int valLum = analogRead(P_LUM);
  int lum = map(valLum, CAL_LUM_MIN, CAL_LUM_MAX, 0,100); // Eclairage en %
  Serial.println(lum);

  // Erreur si -10% CAL_LUM_ON
  if(lum < CAL_LUM_ON-10){
    /*
     * TODO
     * - ERREUR
     * - ERR si +10 % ?
     */
  }
  // ----------

  delay(500);
}

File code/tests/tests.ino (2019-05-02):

// TESTS VENTILO
/*const short PIN = 9;

void setup() {
  Serial.begin(9600);
  Serial.println("START");
  pinMode(PIN,OUTPUT);
  analogWrite(PIN, 255);
}

void loop() {
}*/

// TESTS CAPTEURS
/* const short PIN = 9;
const int PIN_THERM = A0;
const int P_LUM = A3;

int CAL_LUM_MIN = 5,
    CAL_LUM_MAX = 213; // Calibrage Min et Max de la photoresistance slon LED

void setup(){
  Serial.begin(9600);
  Serial.println("START");
  pinMode(PIN,OUTPUT);
  analogWrite(PIN, 255);
}

void loop() {
  analogRead(PIN_THERM); // Lecture dans le vide car valeur inexacte
  int temp = analogRead(PIN_THERM);
  Serial.println(temp);
  // --- LM35DZ
  temp = temp * (5.0 / 1023.0 * 100.0); // Conversion en degrés Celsius
  // ----------
  // --- TMP36
  // temp = map(temp,0,1023,0,5000);// Tension entre 0 et 5000 mV
  // temp = map(temp,0,1750,-57,118); // Tension de 0 à 1750mV en température de -50°C à 125°C;
  // ----------
  Serial.println(temp);


  // --- Luminosité - photorésistance ---
  // int valLum = analogRead(P_LUM);
  // Serial.println(valLum);
  // int lum = map(valLum, CAL_LUM_MIN, CAL_LUM_MAX, 0,100); // Eclairage en %
  // Serial.println(lum);
  Serial.println();

  
  delay(1000);
} */

// TESTS FONCTIONS TRANSFORMATION SECONDES
// -- Fonction générales --
// Transformer temps secondes en HH:MM:SS
/* String time_sec_toStr(unsigned long timeSec){
  unsigned long time[4];
  String timeStr[4];

  // Heures
  time[0] = timeSec/3600;
  timeSec -= 3600*time[0];
  timeStr[0] = String(time[0]);
  timeStr[0] = (time[0]<10)? "0"+timeStr[0] : timeStr[0]; // Rajouter 0 si <10

  // Minutes
  time[1] = timeSec/60;
  timeSec -= 60*time[1];
  timeStr[1] = String(time[1]);
  timeStr[1] = (time[1]<10)? "0"+timeStr[1] : timeStr[1];
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

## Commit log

2019-04-13 All we created in one folder
    [boite-ensemble.scad, boite-ensemble.stl, capot.stl, capot_ecran.scad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]
2019-04-16 More pictures
    [BOM.ods]
2019-04-21 Pause and Stop fully functional + countdown functional + testing LED and fan admin
2019-04-21 + LED and fan control fully functional
2019-04-25 Added sensors (light and temp) + errors
    [face-fermeture.stl, photoreacteur.fzz]
2019-04-29 + implemented temperature, luminosity (nonfonctional) and images
2019-05-02 +temperature and luminosity averages, refreshed menus
    [photoreacteur.fzz]
2019-05-05 1.0 in photoreactor
    [boite-ensemble.stl, capot.stl, capot_ecran.stl, capuchon.stl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]
